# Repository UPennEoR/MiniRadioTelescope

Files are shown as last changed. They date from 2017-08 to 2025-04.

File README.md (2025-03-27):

# Mini Radio Telescope
MRT
A computerized telescope created using a satellite TV dish and hobbyist electronic components.<br/>
This GitHub contains Arduino and Python code for the telescope.

## Hardware
### Electronics
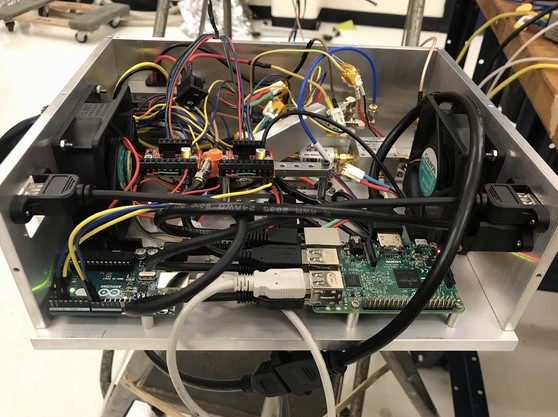
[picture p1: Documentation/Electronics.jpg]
Electronics

* Satellite Dish (with LNB)
* Arduino Uno
* Raspberry Pi
* [Stepper Motors](https://www.sparkfun.com/products/13656)
* [Big Easy Driver](https://www.sparkfun.com/products/12859)

### RF
* [Bias Tee](https://www.minicircuits.com/WebStore/dashboard.html?model=ZFBT-282-1.5A%2B)
* [Lumped LC High Pass Filter, 910 - 3000 MHz](https://www.minicircuits.com/WebStore/dashboard.html?model=SHP-900%2B)
* [LTCC Low Pass Filter, DC - 1200 MHz, 50Ω](https://www.minicircuits.com/WebStore/dashboard.html?model=VLF-1200%2B)
* [Power Detector](https://www.minicircuits.com/WebStore/dashboard.html?model=ZX47-60LN-S%2B)
* [Low Noise Amplifier, 40 - 2600 MHz, 50Ω](https://www.minicircuits.com/WebStore/dashboard.html?model=ZX60-P105LN%2B)
* [RTL-SDR](https://www.amazon.com/RTL-SDR-Blog-RTL2832U-Software-Defined/dp/B0129EBDS2/)

[Detailed Parts List](https://docs.google.com/spreadsheets/d/1V9u7jmuFzU5uZdgKm3iKv23dL2x4DQUVWW0j8lXsqZ8/edit?usp=sharing)

## Maps

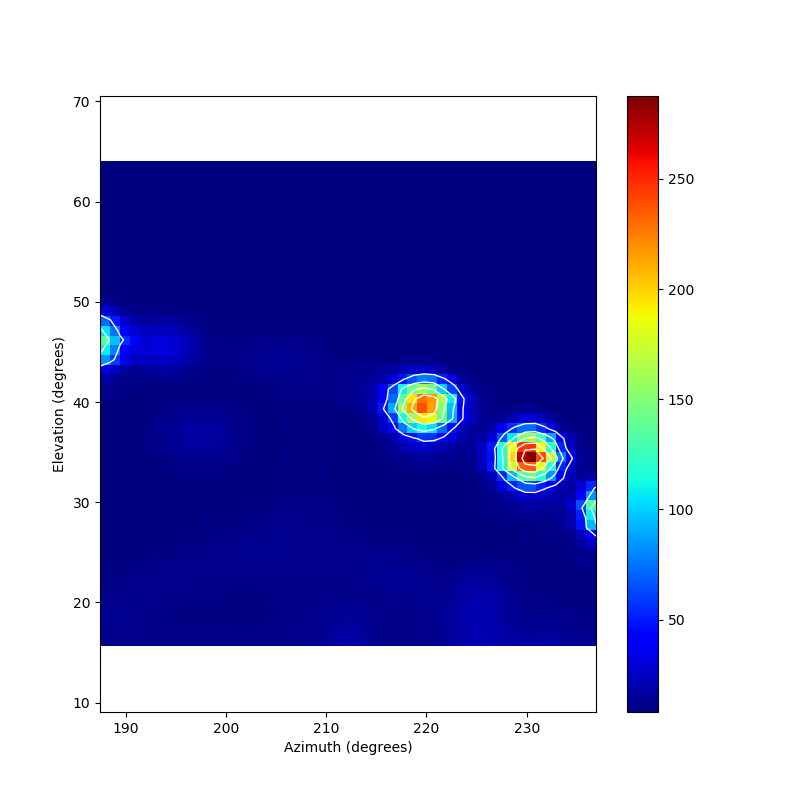
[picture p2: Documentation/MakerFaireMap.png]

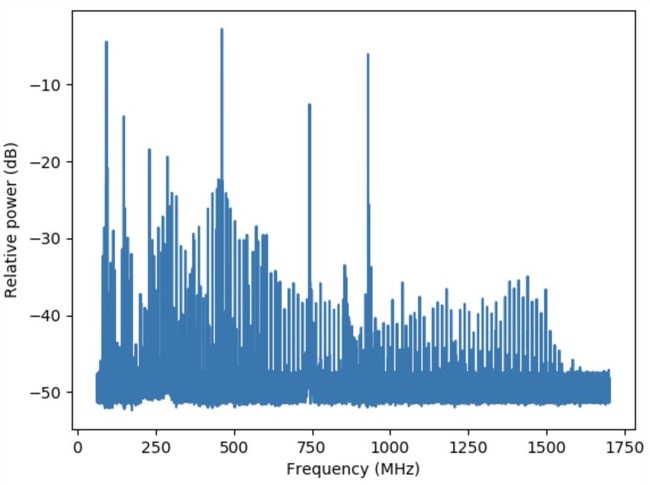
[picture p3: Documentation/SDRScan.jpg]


As of 5 April 2020, the working Arduino sketch is: MRTArduino (previously known as MRTv2)<br/>
The python code for the Pi is MRT_PY4.py

Hackaday was kind enough to do a write-up about this project: https://hackaday.com/2019/10/22/a-miniature-radio-telescope-in-every-backyard/

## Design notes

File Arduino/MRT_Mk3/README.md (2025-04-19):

This is the working version of the Arduino code as of 4/19/2025.  

There are a couple of numbers that are hardcoed:
- serial communication is at 115200 baud `BAUD_RATE`
- loop rate is 4 ms (250 Hz) `dt_loop`

The basic idea is that the Arduino loop continuously sends a certain set of information, namely
- the current counter value
- the number of milliseconds to complete the loop
- ~the last command sent~
- the current azimuth in motor microsteps (convertible but not converted to angle)
- the current elevation in motor microsteps (convertible but not converted to angle)
- the analog voltage at the AIN0 input
- a toggle bit for whether a (move) command is currently executing

Commands are 12 characters long and must be enclosed in <> as `<xxxxxxxxxxxx>`

<X> is the abort command, which stops all motion, and violates the 12 character rule.

Axis / Sense / Microstep / Clock cycles per step / Number of steps

0: 'a' azimuth or 'e' elevation
1: +/-
2: m: 1/16, e: 1/8 q: 1/4 h: 1/2 f: 1
3 - 6: the number of clock cycles 
7 - 11: number of steps.  This sets the max at one go to 99999

The C code necessary to read the Arduino output:

Install hdf5:
sudo apt install libhdf5-dev
sudo apt install hdf5-tools

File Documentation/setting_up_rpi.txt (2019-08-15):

Seems like Anaconda / Miniconda is not the way to go for RPi.

https://www.raspberrypi.org/documentation/linux/software/python.md

How to build a kind of minimal stack

https://geoffboeing.com/2016/03/scientific-python-raspberry-pi/

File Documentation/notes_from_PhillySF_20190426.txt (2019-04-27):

Arduino used previously lights up same as a working one, but I can't
seem to connect to it.  :( Not clear if this has anything to do with
powering it from the 9V regulator or not.

Now using
/anaconda3/bin/python
Working in base ... I might end up regretting that.
Note that this is a new Anaconda install since last used.

Apparently `serial` is not a standard install with Anaconda?

(base) modv-ve503-1809:MiniRadioTelescope jaguirre$ python MRT_PY3.py 
Traceback (most recent call last):
  File "MRT_PY3.py", line 6, in <module>
    import MRT_FUNC_PY3 as mrtf
  File "/Users/jaguirre/Software/MiniRadioTelescope/MRT_FUNC_PY3.py", line 8, in <module>
    import serial
ModuleNotFoundError: No module named 'serial'

conda install pyserial

DEATH TO PEOPLE WHO NAME THEIR PACKAGES DIFFERENT NAMES THAN THE IMPORT NAME!!!

Nice!  Not having the position sensor not connected is OK!

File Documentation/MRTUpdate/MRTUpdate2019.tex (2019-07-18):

\documentclass[11pt,letterpaper]{spie}

% Commonly used packages
\usepackage{natbib}
\usepackage{epsfig}
\usepackage{graphicx}
\usepackage{pgf}  
\usepackage{caption}
\usepackage{multirow}
\usepackage[normalem]{ulem}
\usepackage{color}
\usepackage{pdfpages}
\usepackage[breaklinks,colorlinks=true, pdfstartview=FitV, linkcolor=blue, 
            citecolor=blue, urlcolor=blue]{hyperref}
\usepackage{rotating}
\usepackage{url}
\usepackage{amsmath}
\usepackage{amssymb}
\usepackage{bm}

% Bibliography
%\bibliographystyle{apj_w_etal}
%\citestyle{aa}
%\include{journals}
%\pagenumbering{arabic}
%\pagestyle{plain}

\thispagestyle{empty}
% ------------------- Title and Author -----------------------------
\title{The Mini Radio Telescope (MRT):\\
A Tool for Education and Outreach}
%\author{James Aguirre}

\begin{document}

\maketitle

The Mini Radio Telescope funded by this grant is designed to be a portable demonstration and teaching tool.  This year it was was demonstrated at Boys' Latin High School, used in Prof. Aguirre's ASTR250 course at Penn, used as part of the Experimental Physics Research Academy summer program for high school students at Penn, and used in public demonstrations at the Philadelphia Science Festival both in Clark Park and on Philadelphia Parkway.

\begin{figure}[h]
\centering
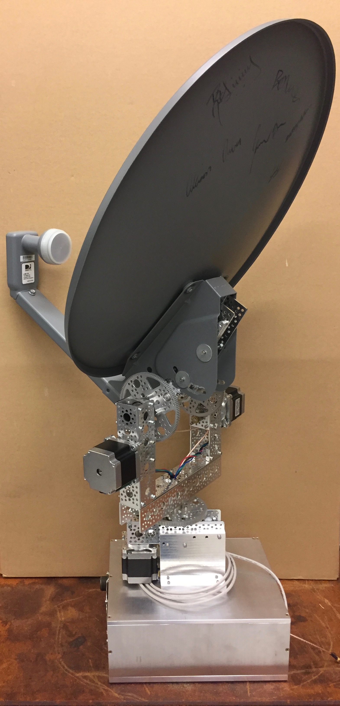
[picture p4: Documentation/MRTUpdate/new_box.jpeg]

\vspace{5pt}
\caption{The current mechanical design from hobby electronics components (Actobotics) was simple and quick, but insufficiently rigid.
}
\label{fig:Devices}
\end{figure}

\begin{figure}[h]
\centering
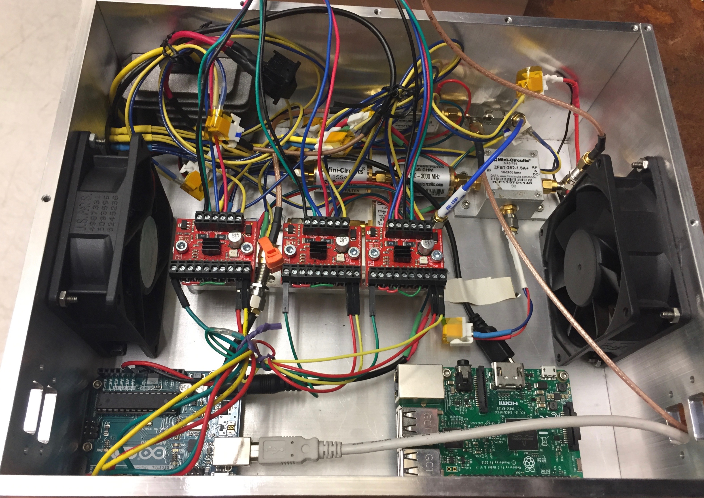
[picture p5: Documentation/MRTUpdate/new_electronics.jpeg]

\vspace{5pt}
\caption{The new electronics are housed in an enclosure designed to be more rugged.
}
\label{fig:Devices}
\end{figure}

\begin{figure}[h]
\centering
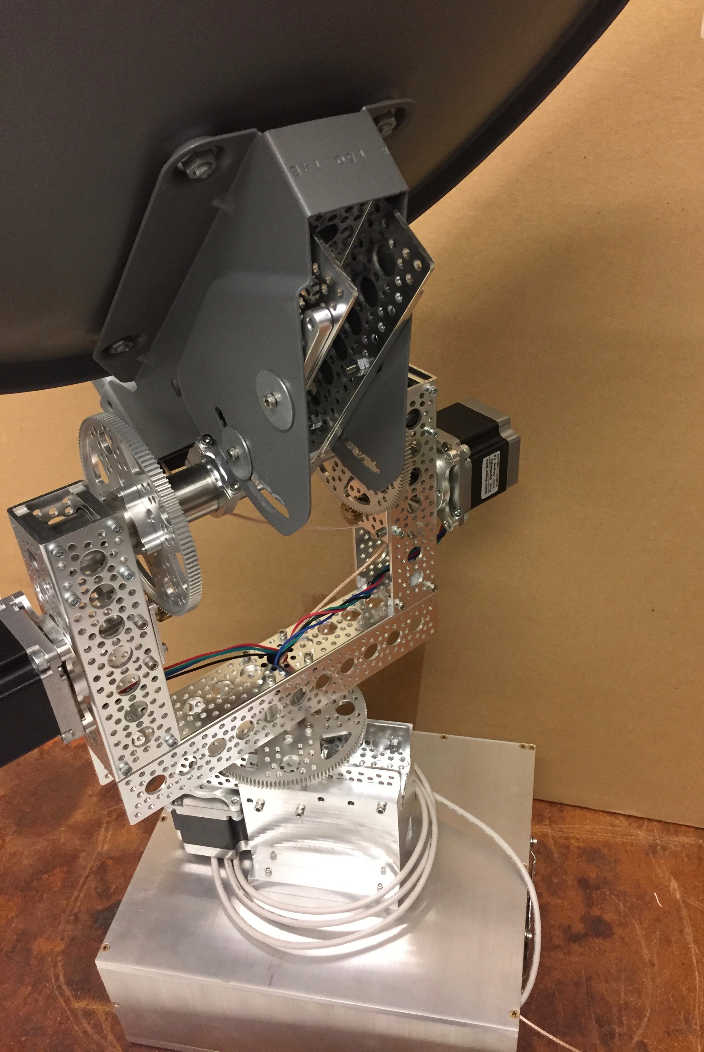
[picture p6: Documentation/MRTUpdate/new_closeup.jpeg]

\vspace{5pt}
\caption{The current mechanical design from hobby electronics components (Actobotics) was simple and quick, but insufficiently rigid.
}
\label{fig:Devices}
\end{figure}

\begin{figure}[h]
\centering
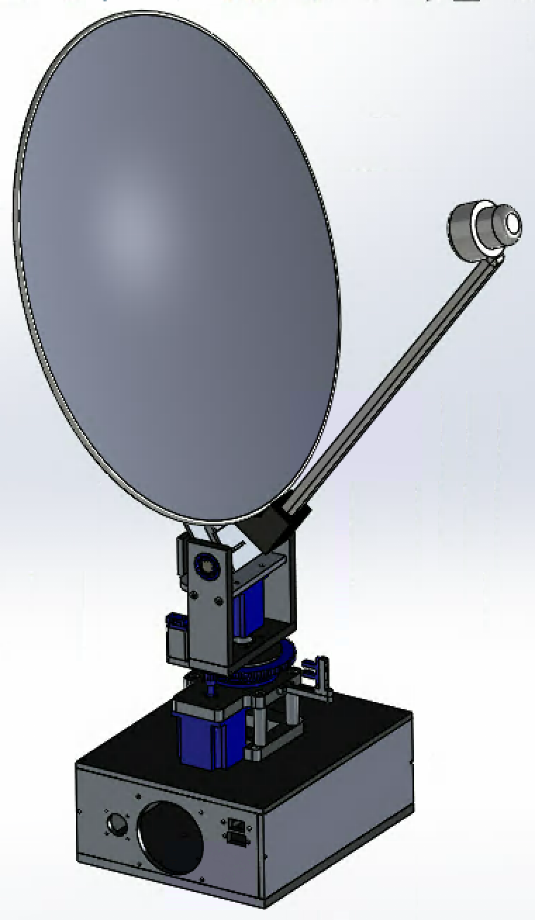
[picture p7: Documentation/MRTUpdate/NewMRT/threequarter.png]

\vspace{5pt}
\caption{The new simplified MRT telescope mount design.}
\label{fig:NewMRTthreequarter}
\end{figure}

\begin{figure}[h]
\centering
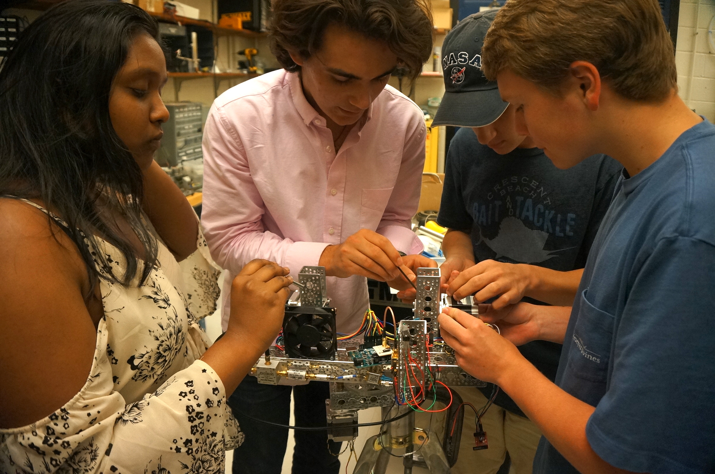
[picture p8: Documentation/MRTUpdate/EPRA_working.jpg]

\vspace{5pt}
\caption{EPRA students working on the MRT, summer 2017.}
\label{fig:Devices}
\end{figure}

\begin{figure}[h]
\centering
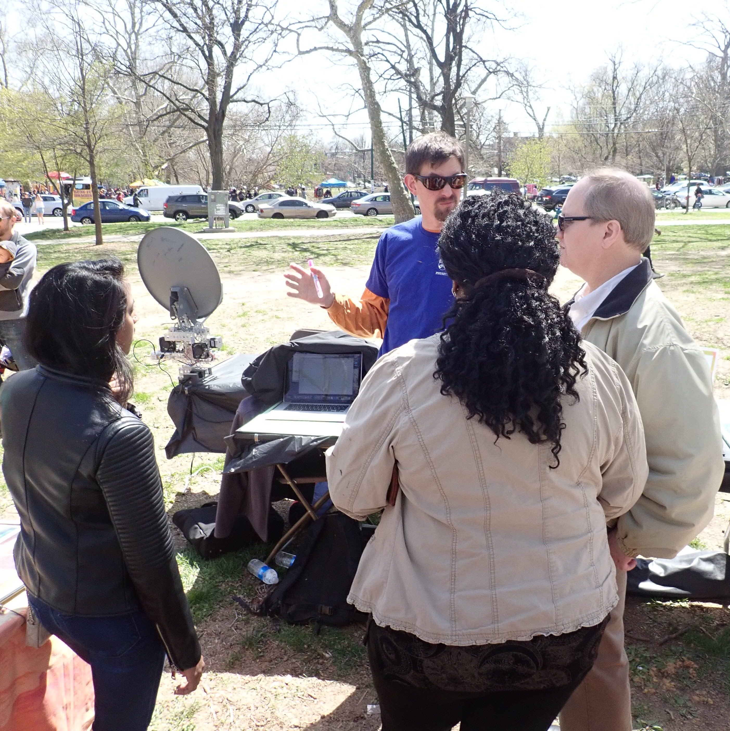
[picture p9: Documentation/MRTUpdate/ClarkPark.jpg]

\vspace{5pt}
\caption{Prof.~Aguirre with the MRT in Clark Park as part of the Philadelphia Science Festival, 21 April 2018.}
\label{fig:ClarkPark}
\end{figure}

\begin{figure}[h]
\centering
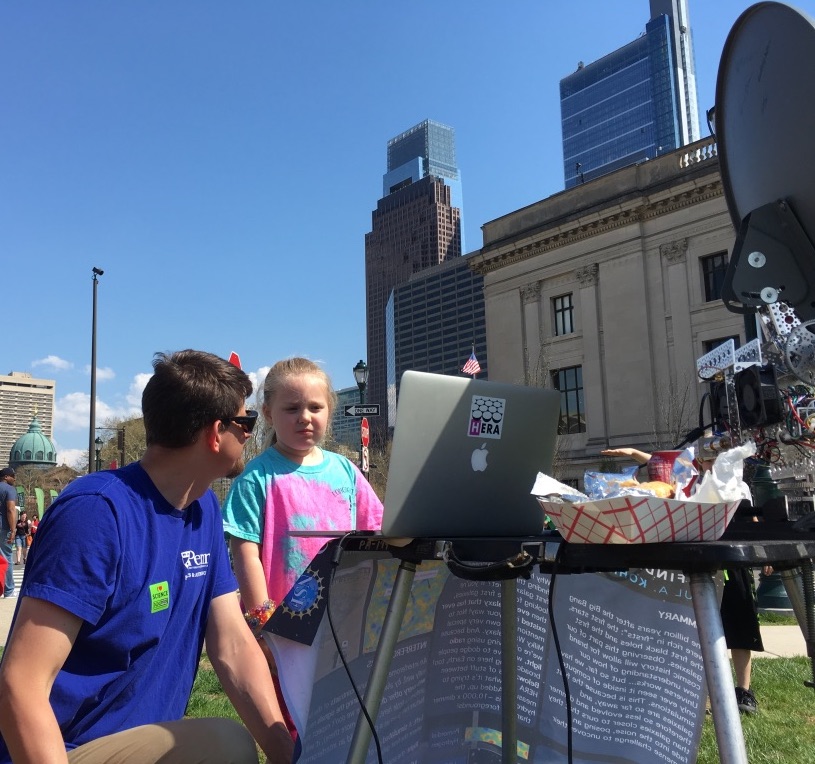
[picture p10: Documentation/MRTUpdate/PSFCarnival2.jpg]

\vspace{5pt}
\caption{Explaining the telescope to a young visitor to the Philadelphia Science Festival's Carnival, 28 April 2018.}
\label{fig:Devices}
\end{figure}

\end{document}

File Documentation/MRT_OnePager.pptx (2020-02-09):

## Mini Radio Telescope James Aguirre jaguirre@sas.upenn.edu Open source software at https://github.com/upenneor/miniradiotelescope

Raspberry Pi: runs the main control program and processes the data
Arduino: digitizes the signal from the radio receiver and communicates with the motor controllers to move the telescope
Radio filters and amplifiers: boost the signal from the commercial electronics and convert to a measurement of total power
Software defined radio (SDR): can make a spectrum of the received radio signal
Motor controllers: one for each axis of elevation and azimuth

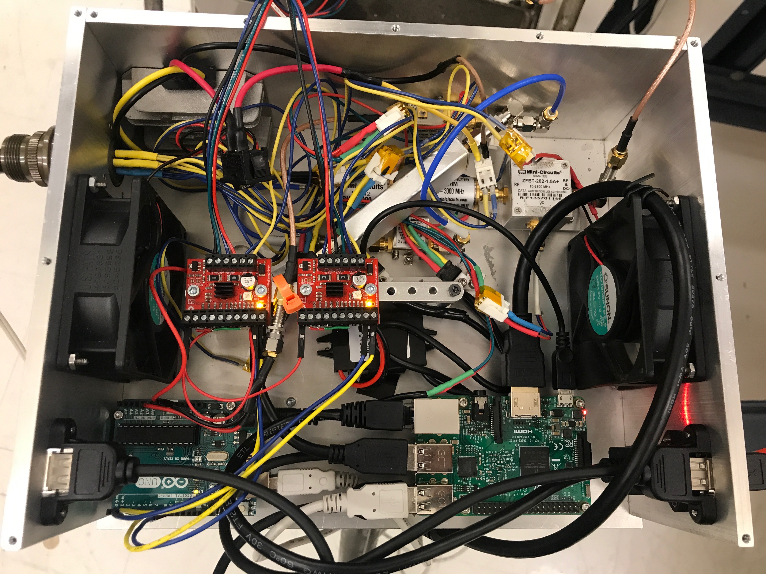
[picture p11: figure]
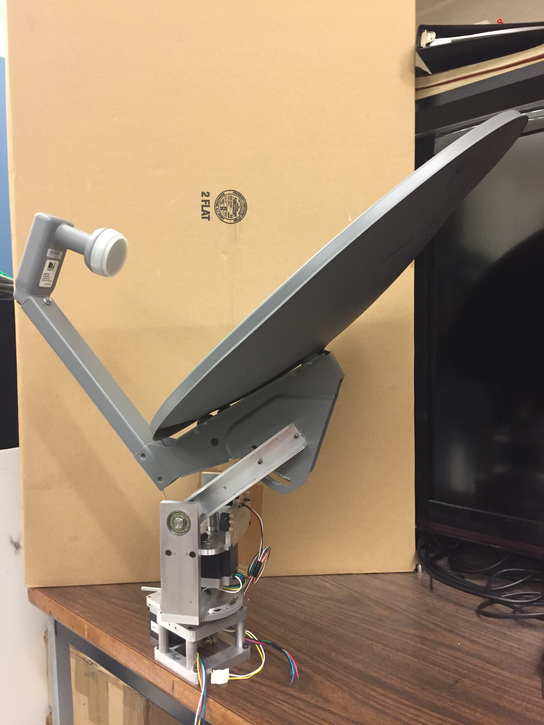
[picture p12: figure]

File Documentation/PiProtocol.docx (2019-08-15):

Raspberry Pi Set-up

On another (Linux) machine which can access the SD card:

Loading Operating System

1) To determine the name of the SD card

-Open Terminal

-type ‘df -h’ without the quotes before inserting card

-A list of mounted devices will appear

-Insert card and type ‘df -h’ again. The newly listed device is the name of the SD card.

-For example, ours was listed as ‘/dev/mmcblk0p1’

-Note: the name of the card is ‘mmcblk0’ and the partition designation is ‘p1’

2) Unmount card

-type ‘umount’ followed by the full name of your SD card

-For example, ours would be ‘ umount /dev/mmcblk0p1’

3) Download the latest OS released by Raspberry Pi

-At the time this is being written, the latest release is “Raspian Jessie with Pixel”

-This OS weighs 4.3 GB.

-Extract the file and make note of the name and location of the file

-Ex: ‘2016-09-23-raspian-jessie.img’ located under ‘/home/dmauri’

4) Install OS image on SD card

- ‘sudo dd bs=4M if=2016-09-23-raspian-jessie.img of=/dev/mmcblk0’

-sudo gives permission if you aren’t logged in as root

-USE CAUTION WHEN USING THE COMMAND dd

-If used improperly, the operating system on your current device can be erased

-After ‘if=’ type in the file name of the OS image to be loaded

-After ‘of=’ type in the name of the SD card without the partition index

-Note: At this point terminal will stop responding. It will not demonstrate how much progress has been made. To check on progress, open another Terminal window and type ‘sudo pkill -USR1 -n -x dd’

-When the system has finished writing the image to the card, it will generate a report such as:

‘1036+1 records in

1036+1 records out

4348444672 bytes (4.3 GB, 4.0 GiB) copied, 799.367 s, 5.4 MB/s

5) Synchronize and Eject Card

-type in ‘Sync’

-This will pull down everything that was left in the cache so that you can unmount

-Unmount card using the previously indicated umount command.

For the Pi itself:

Getting MAC Address

MAC Address is often required to establish Internet connection

1) In terminal type ‘ifconfig eth0’

-This will generate a report. Look for the the line:

‘eth0 Link encap: Ethernet HWaddr ’

-The characters following HWaddr is the MAC Address

Installing Arduino IDE

1) In terminal type ‘sudo apt-get install arduino’

-Installation will take time but upon completion can be accessed via terminal or from the menu.

Installing Miniconda

1) In terminal type the following in the listed order:

-‘wget http://repo.continuum.io/miniconda/Miniconda-3.5.5-Linux-armv6l.sh’

-‘md5sum Miniconda-3.5.5-Linux-armv6l.sh’

-This should return something like ‘2f37cb775ec3e482280a7bd6b97ee501’

-‘/bin/bash Miniconda-3.5.5-Linux-armv6l.sh’

Should also add git and emacs

sudo apt-get install git

Figuring out which port the Arduino is on

Hi Mauricio,

I’ve looked into making the ltr-sdr library that you pointed out yesterday. You can use the directions here: http://osmocom.org/projects/sdr/wiki/rtl-sdr. Basically the steps I followed were:

- git clone https://github.com/librtlsdr/librtlsdr.git

- cd librtlsdr

- mkdir build

- cd build

- cmake ../

- make

- sudo make install

- sudo ldconfig

This approach requires having `cmake` installed, so you might need to get that from somewhere. I also had to install `libusb`, which I did via MacPorts. Let me know if you have any questions about things, and we can work through them.

-Paul

Starting from scratch

Download NOOBS

https://www.raspberrypi.org/downloads/noobs/

(What is Raspberry Pi Desktop? https://www.raspberrypi.org/downloads/raspberry-pi-desktop/)

Needed a proper SD formatter

https://www.sdcard.org/downloads/formatter/

Formatted SD FAT-32

Copied NOOBS from unzipped file to SD

Booted RPi and chose Raspbian (only option if not connected online?)

(Scratch programming language?)

https://geoffboeing.com/2016/03/scientific-python-raspberry-pi/

For RTLSDR …

sudo apt-get install cmake

git clone https://github.com/librtlsdr/librtlsdr.git

cd librtlsdr

mkdir build

cd build

sudo apt-get install libusb-1.0

cmake ../ -DINSTALL_UDEV_RULES=ON -DDETACH_KERNEL_DRIVER=ON

make

sudo make install

sudo ldconfig

Installing jupyter

https://www.instructables.com/id/Jupyter-Notebook-on-Raspberry-Pi/

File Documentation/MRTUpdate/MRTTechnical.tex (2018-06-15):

\documentclass[11pt,letterpaper]{spie}

% Commonly used packages
\usepackage{natbib}
\usepackage{epsfig}
\usepackage{graphicx}
\usepackage{pgf}  
\usepackage{caption}
\usepackage{multirow}
\usepackage[normalem]{ulem}
\usepackage{color}
\usepackage{pdfpages}
\usepackage[breaklinks,colorlinks=true, pdfstartview=FitV, linkcolor=blue, 
            citecolor=blue, urlcolor=blue]{hyperref}
\usepackage{rotating}
\usepackage{url}
\usepackage{amsmath}
\usepackage{amssymb}
\usepackage{bm}

% Bibliography
%\bibliographystyle{apj_w_etal}
%\citestyle{aa}
%\include{journals}
%\pagenumbering{arabic}
%\pagestyle{plain}

\thispagestyle{empty}
% ------------------- Title and Author -----------------------------
\title{The Mini Radio Telescope (MRT):\\
Technical Update}
%\author{James Aguirre}

\begin{document}

\maketitle

The Mini Radio Telescope has now reached reasonable technical maturity, and we are working to make it completely robust for demonstrations, and capable of production in modest numbers.

The software is available publicly at \url{https://github.com/UPennEoR/MiniRadioTelescope}.

\begin{figure}[h]
\centering
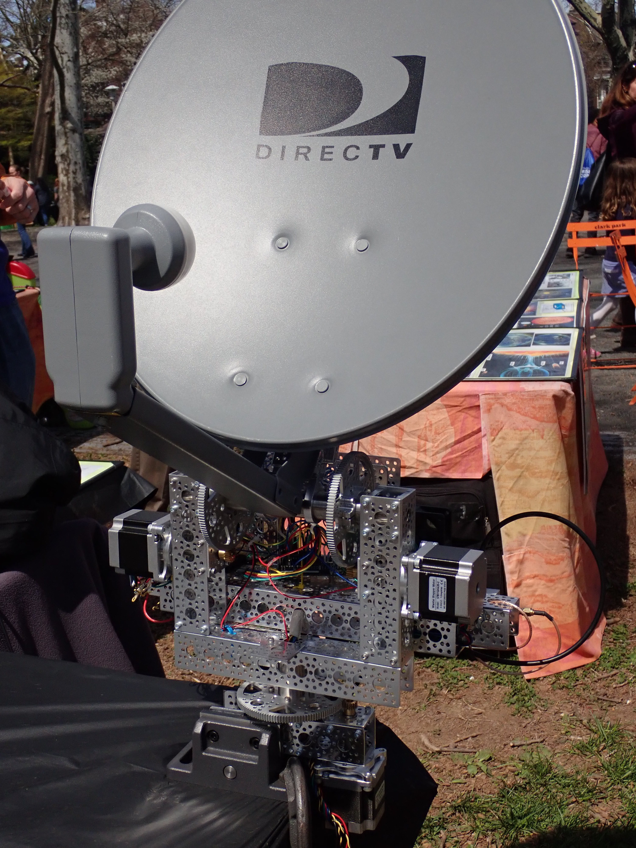
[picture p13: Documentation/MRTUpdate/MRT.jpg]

\vspace{5pt}
\caption{The Mini Radio Telescope in the spring of 2018.  All the components are commercially available and can be assembled with a minimal set of tools.}
\label{fig:Devices}
\end{figure}

\begin{figure}[h]
\centering
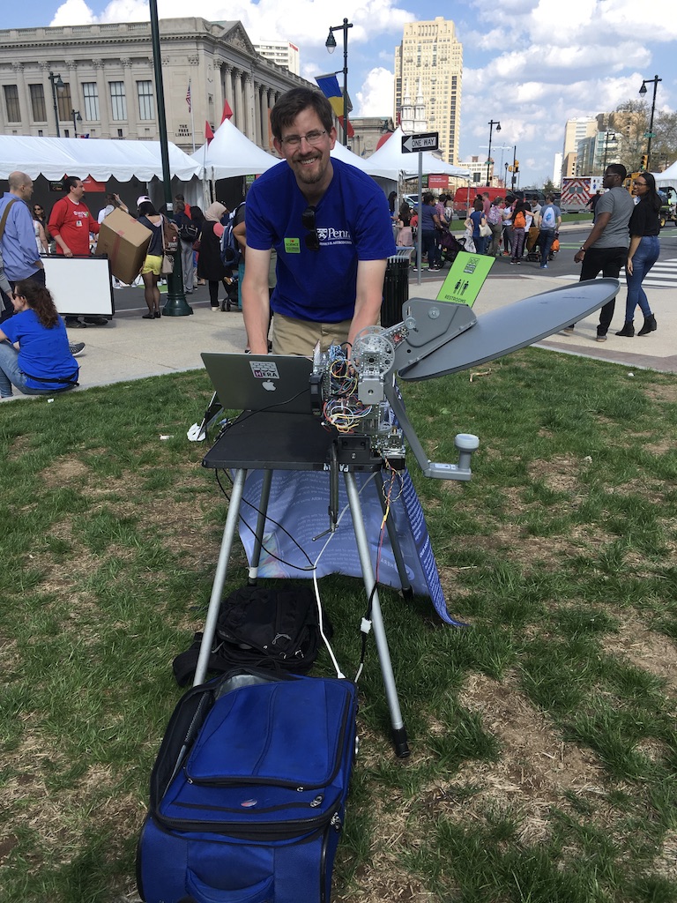
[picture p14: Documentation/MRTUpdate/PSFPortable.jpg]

\vspace{5pt}
\caption{The portable setup for the MRT on the Philadelphia Parkway for the Science Carnival.}
\label{fig:Devices}
\end{figure}

\begin{figure}[h]
\centering
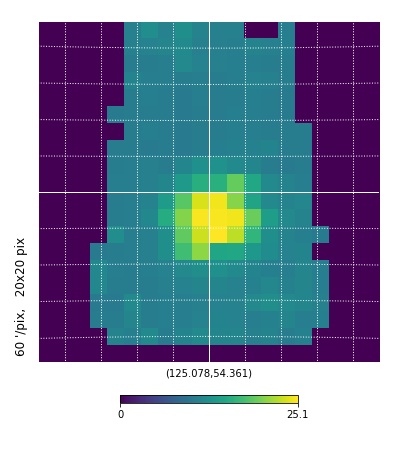
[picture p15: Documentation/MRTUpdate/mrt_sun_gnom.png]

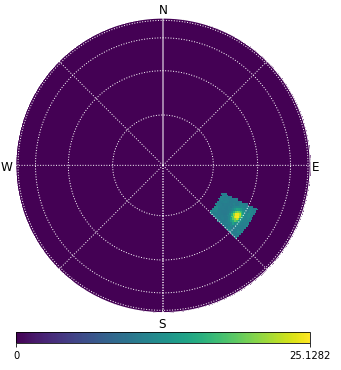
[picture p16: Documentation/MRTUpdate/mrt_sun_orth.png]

\vspace{5pt}
\caption{An MRT map of the sun.  Left: zoom in at the sun's location in altitude / elevation coordinates.   The resolution of the telescope ($5^\circ$) is larger than the true angular size of the sun ($0.5^\circ$).  Right: a view of the entire visible hemisphere showing the location of the mapped region.}
\label{fig:Sun}
\end{figure}

\begin{figure}[h]
\centering
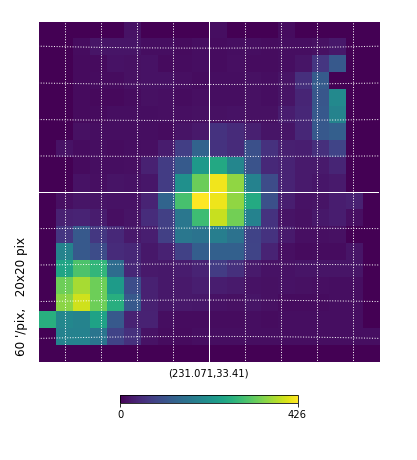
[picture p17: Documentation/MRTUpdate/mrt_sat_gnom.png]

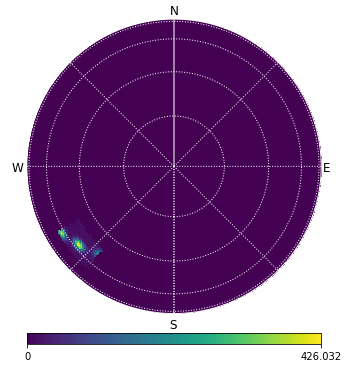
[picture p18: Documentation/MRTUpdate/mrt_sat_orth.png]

\vspace{5pt}
\caption{An MRT map of several geostationary satellites.  Same format as the Figure \ref{fig:Sun}.}
\label{fig:Satellites}
\end{figure}

%\bibliography{/Users/jaguirre/Documents/Latex/MasterReferences}

\end{document}

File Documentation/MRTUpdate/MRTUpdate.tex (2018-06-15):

\documentclass[11pt,letterpaper]{spie}

% Commonly used packages
\usepackage{natbib}
\usepackage{epsfig}
\usepackage{graphicx}
\usepackage{pgf}  
\usepackage{caption}
\usepackage{multirow}
\usepackage[normalem]{ulem}
\usepackage{color}
\usepackage{pdfpages}
\usepackage[breaklinks,colorlinks=true, pdfstartview=FitV, linkcolor=blue, 
            citecolor=blue, urlcolor=blue]{hyperref}
\usepackage{rotating}
\usepackage{url}
\usepackage{amsmath}
\usepackage{amssymb}
\usepackage{bm}

% Bibliography
%\bibliographystyle{apj_w_etal}
%\citestyle{aa}
%\include{journals}
%\pagenumbering{arabic}
%\pagestyle{plain}

\thispagestyle{empty}
% ------------------- Title and Author -----------------------------
\title{The Mini Radio Telescope (MRT):\\
A Tool for Education and Outreach}
%\author{James Aguirre}

\begin{document}

\maketitle

The Mini Radio Telescope funded by this grant is designed to be a portable demonstration and teaching tool.  This year it was was demonstrated at Boys' Latin High School, used in Prof. Aguirre's ASTR250 course at Penn, used as part of the Experimental Physics Research Academy summer program for high school students at Penn, and used in public demonstrations at the Philadelphia Science Festival both in Clark Park and on Philadelphia Parkway.

\begin{figure}[h]
\centering
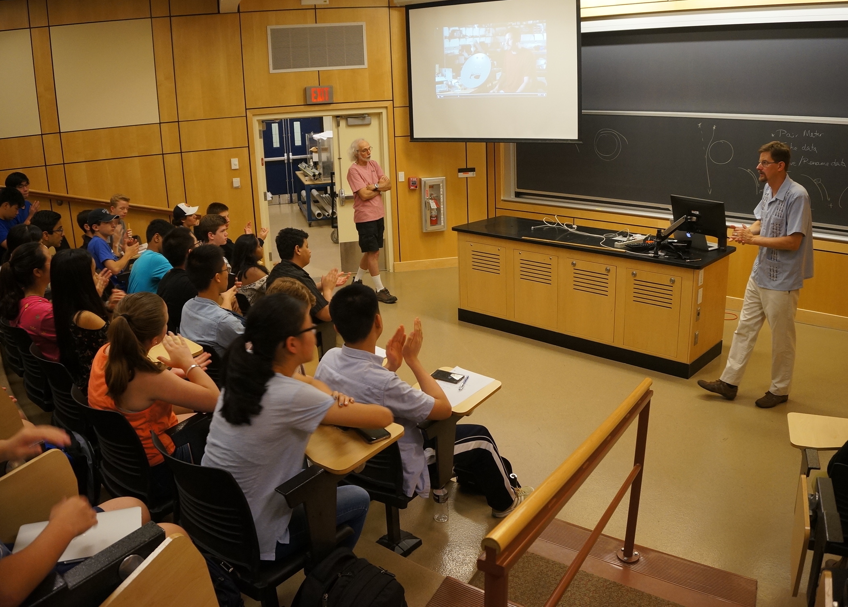
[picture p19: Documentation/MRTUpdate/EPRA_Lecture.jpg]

\vspace{5pt}
\caption{Prof.~Aguirre delivering a lecture to the high school students of the Experimental Physics Research Academy at Penn, Summer 2017.  
%The projected image is of the video describing his work at \url{https://penntoday.upenn.edu/spotlights/building-community-radio-telescope-west-philly}, but the video seems to have disappeared.
}
\label{fig:Devices}
\end{figure}

\begin{figure}[h]
\centering
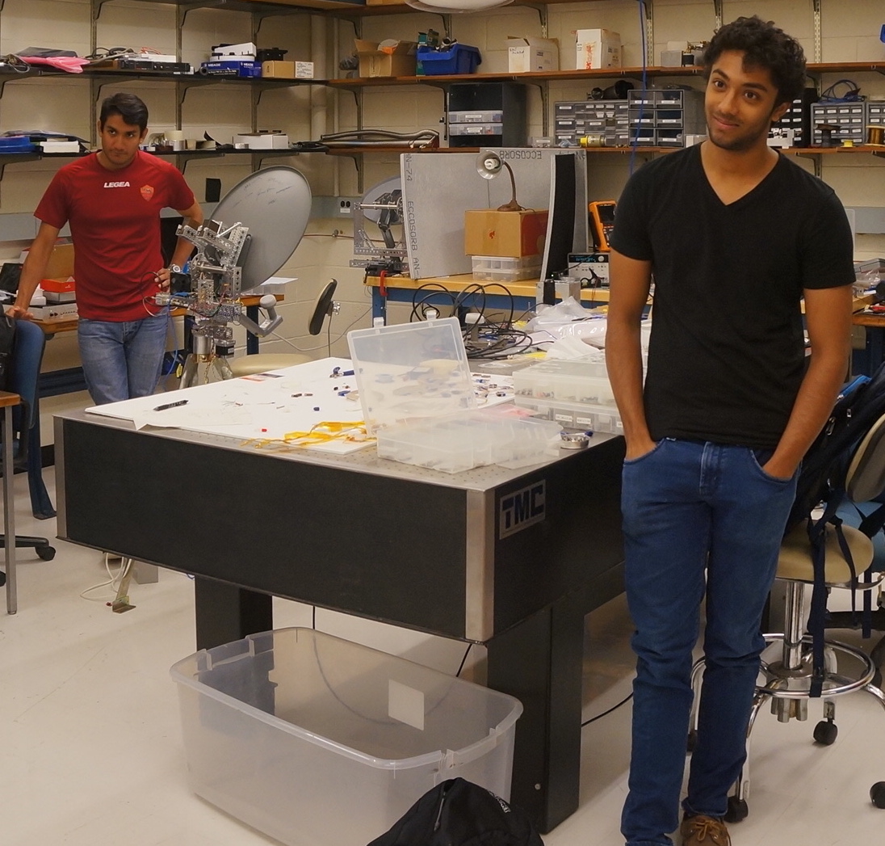
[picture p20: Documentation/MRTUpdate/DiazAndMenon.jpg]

\vspace{5pt}
\caption{Undergraduate research assistants Mauricio Diaz (left) and Viruj Menon (right) prepare to welcome the EPRA students.}
\label{fig:Devices}
\end{figure}

\begin{figure}[h]
\centering

\vspace{5pt}
\caption{EPRA students working on the MRT, summer 2017.}
\label{fig:Devices}
\end{figure}

\begin{figure}[h]
\centering

\vspace{5pt}
\caption{Prof.~Aguirre with the MRT in Clark Park as part of the Philadelphia Science Festival, 21 April 2018.}
\label{fig:ClarkPark}
\end{figure}

\begin{figure}[h]
\centering

\vspace{5pt}
\caption{Explaining the telescope to a young visitor to the Philadelphia Science Festival's Carnival, 28 April 2018.}
\label{fig:Devices}
\end{figure}

\end{document}

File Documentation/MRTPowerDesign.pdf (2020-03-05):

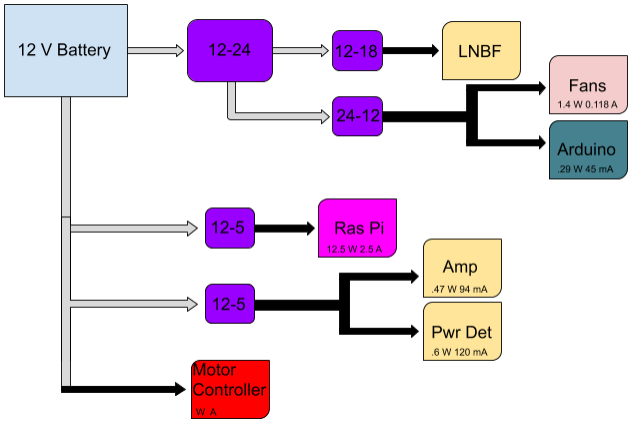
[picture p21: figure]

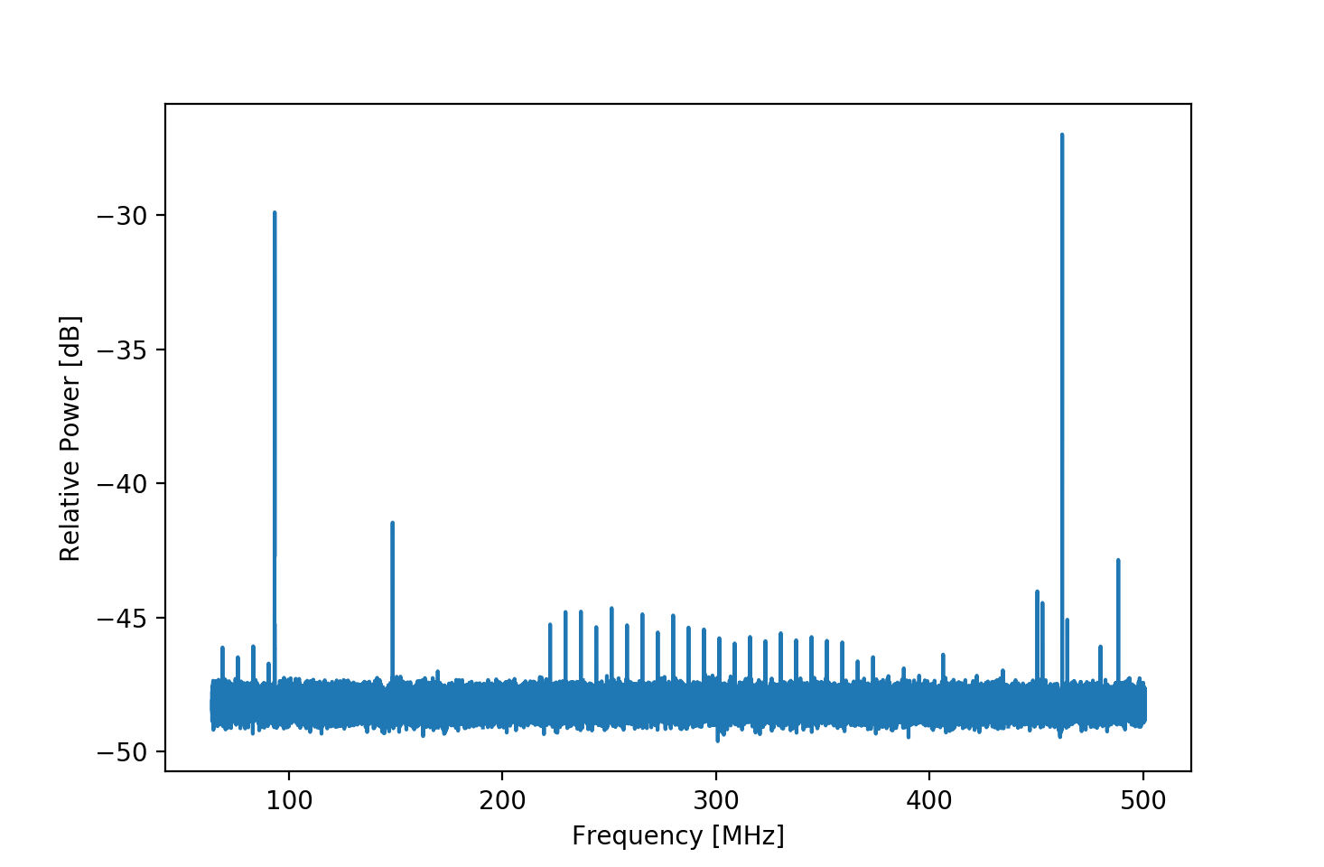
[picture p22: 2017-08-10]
Plots/SDR_Spectrum.png

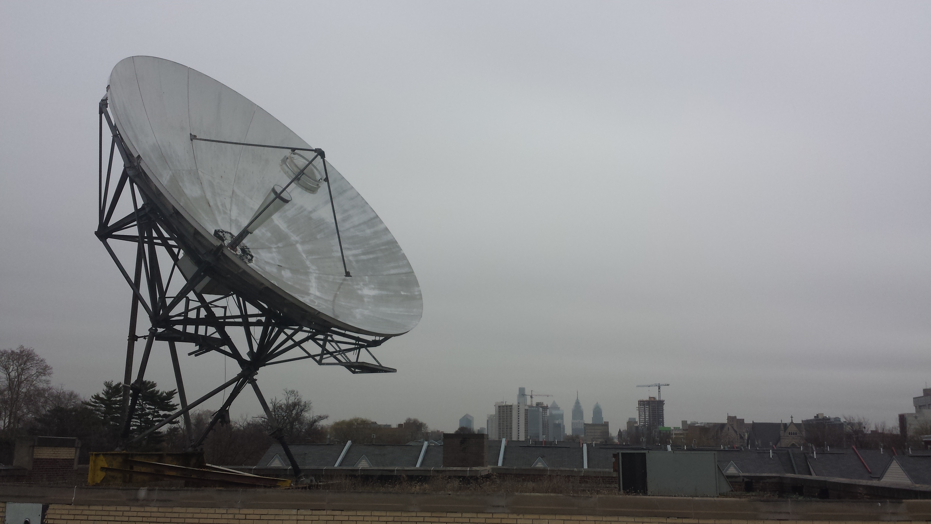
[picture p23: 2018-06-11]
PCRT/Design/Optics/TECDish/PCRT_Image_for_Scaffolding.jpg

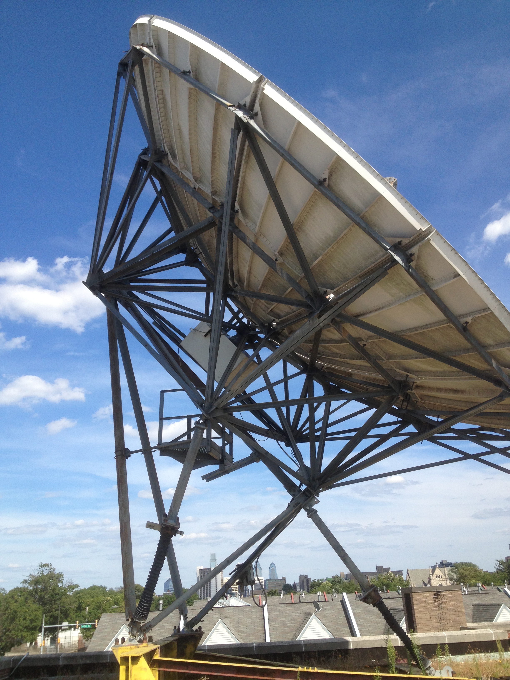
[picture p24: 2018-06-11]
PCRT/Design/Optics/TECDish/photo.JPG

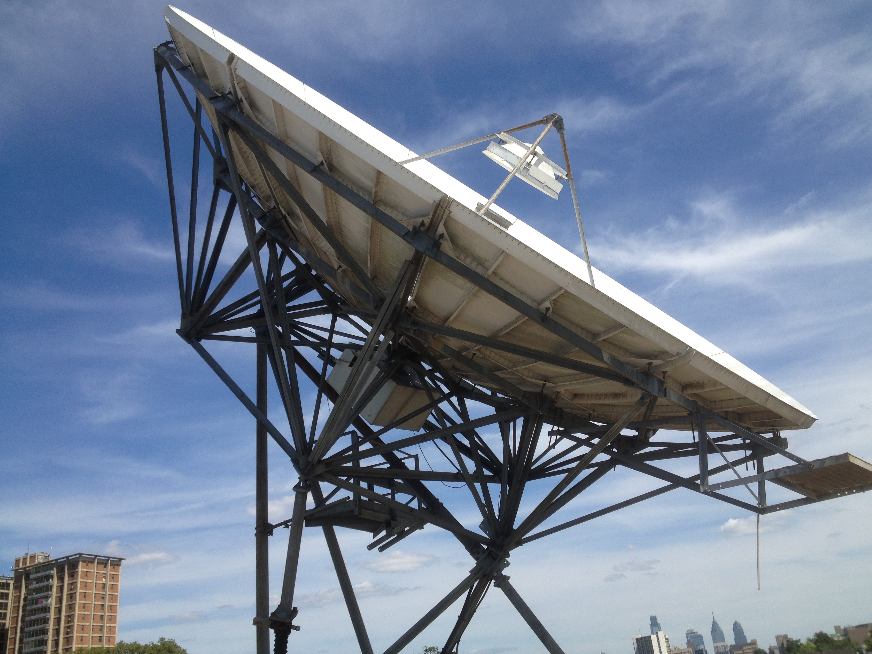
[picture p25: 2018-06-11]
PCRT/Design/Optics/TECDish/PCRT_Image_for_Optics_Determination.jpg

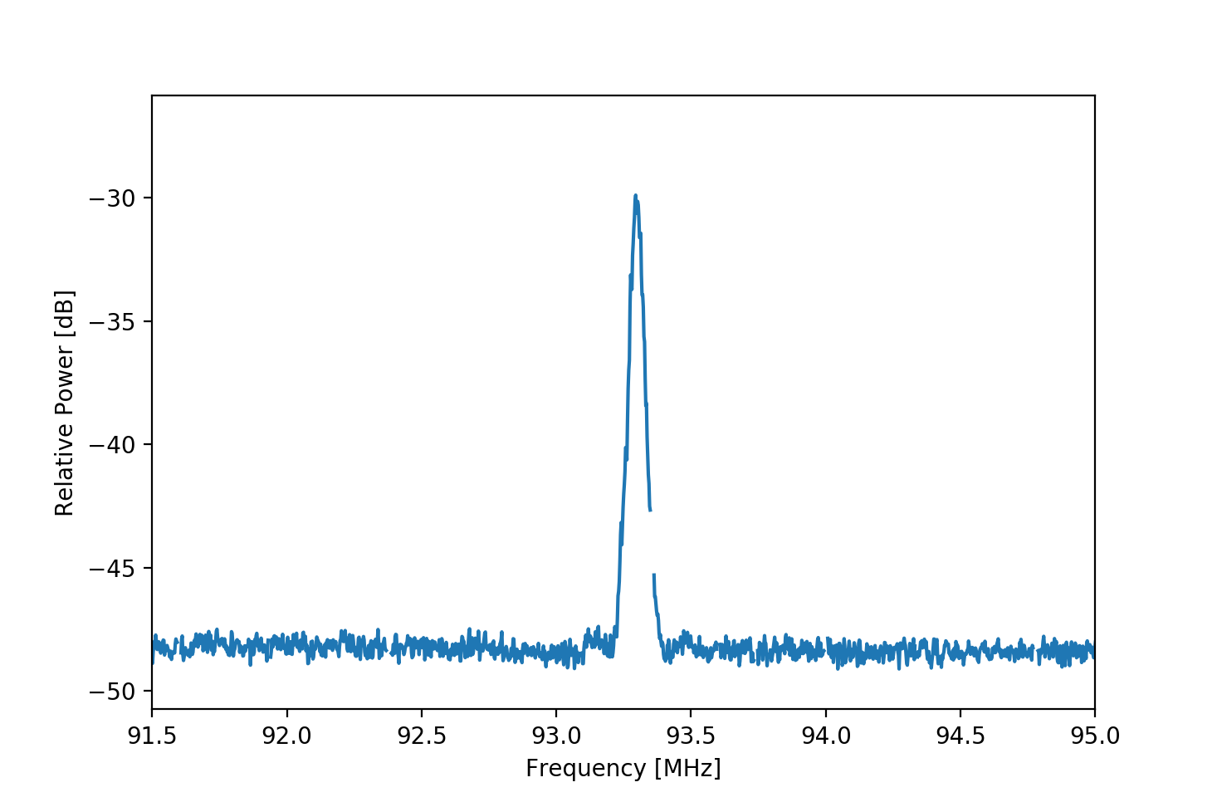
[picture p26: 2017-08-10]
Plots/SDR_Spectrum_Zoom1.png

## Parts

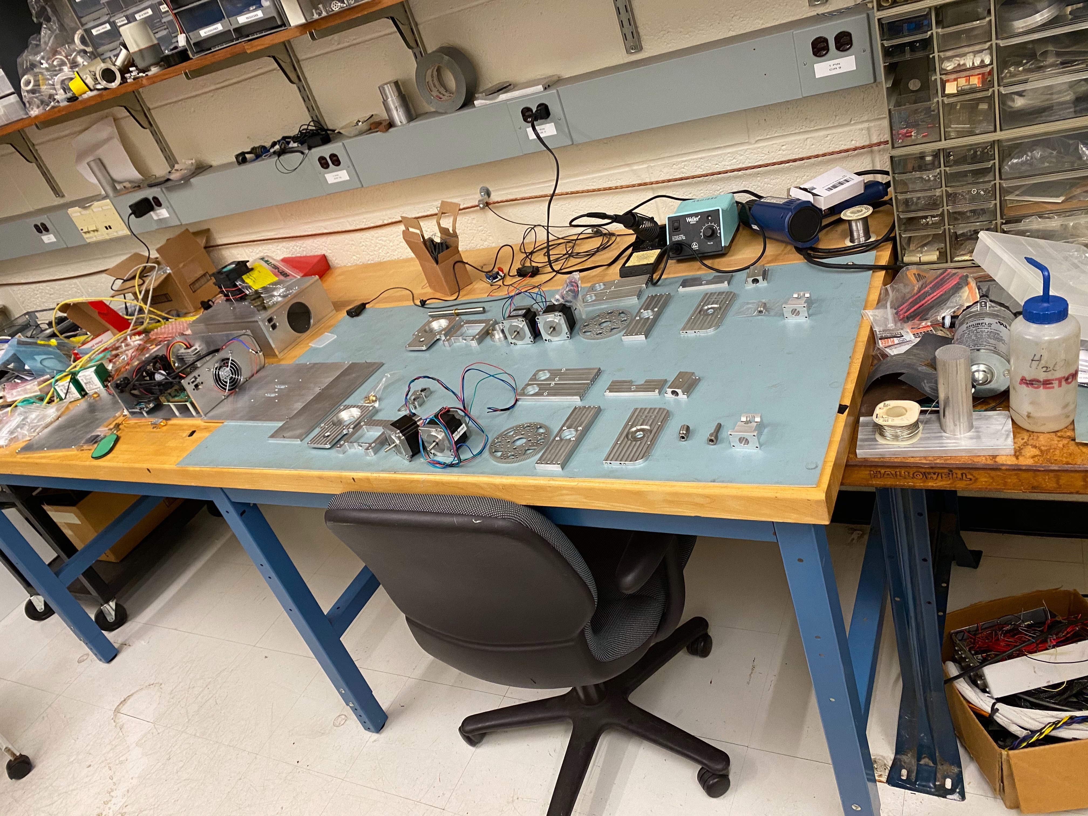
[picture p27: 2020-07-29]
Documentation/MRT_parts_July2020.jpg

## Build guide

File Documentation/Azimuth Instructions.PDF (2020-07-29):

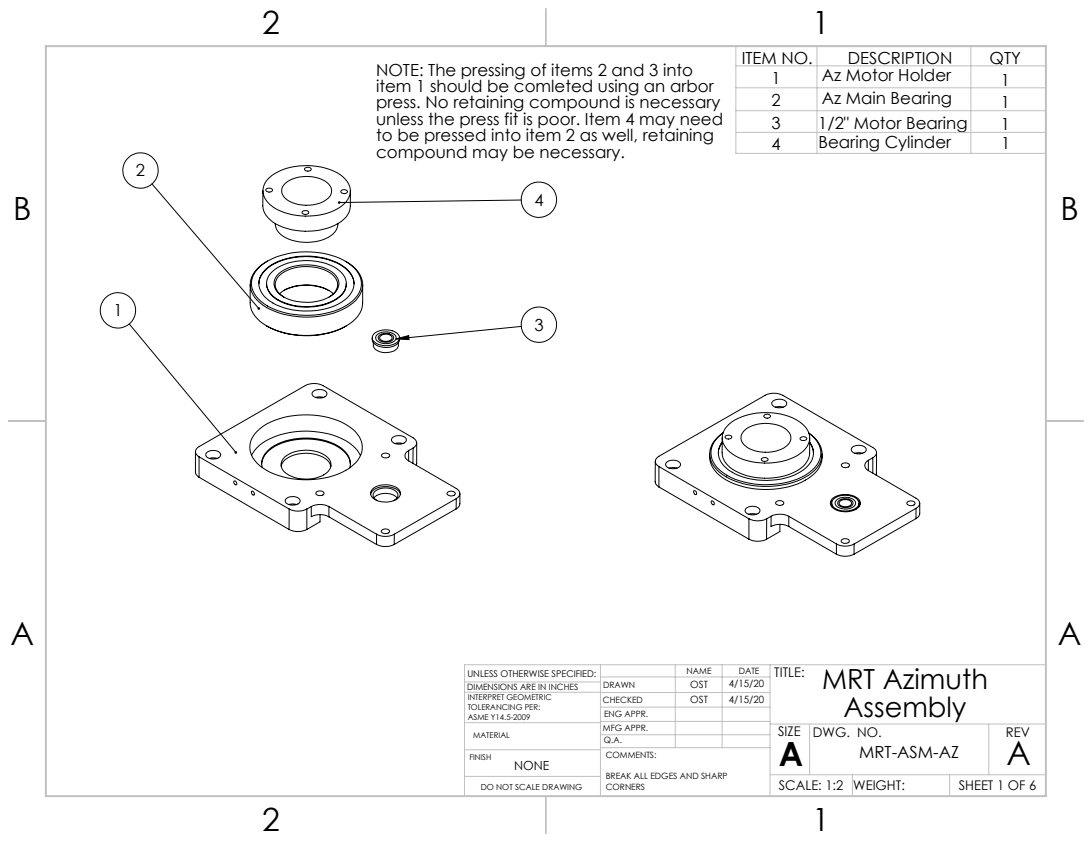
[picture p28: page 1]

ITEM NO. | DESCRIPTION | QTY
1 | Az Motor Holder | 1
2 | Az Main Bearing | 1
3 | 1/2" Motor Bearing | 1
4 | Bearing Cylinder | 1

NOTE: The pressing of items 2 and 3 into
item 1 should be comleted using an arbor
press. No retaining compound is necessary
unless the press fit is poor. Item 4 may need
to be pressed into item 2 as well, retaining
compound may be necessary.

UNLESS OTHERWISE SPECIFIED: | | NAME | DATE | MRT Azimuth TITLE: Assembly
MATERIAL | MFG APPR. | | | SIZE A | DWG. NO. MRT-ASM-AZ | REV A

DRAWN | OST | 4/15/20

DIMENSIONS ARE IN INCHES

INTERPRET GEOMETRIC TOLERANCING PER: ASME Y14.5-2009 | CHECKED | OST | 4/15/20

ENG APPR.

NONE FINISH | COMMENTS: BREAK ALL EDGES AND SHARP CORNERS

DO NOT SCALE DRAWING | | SCALE: 1:2 | WEIGHT: | SHEET 1 OF 6

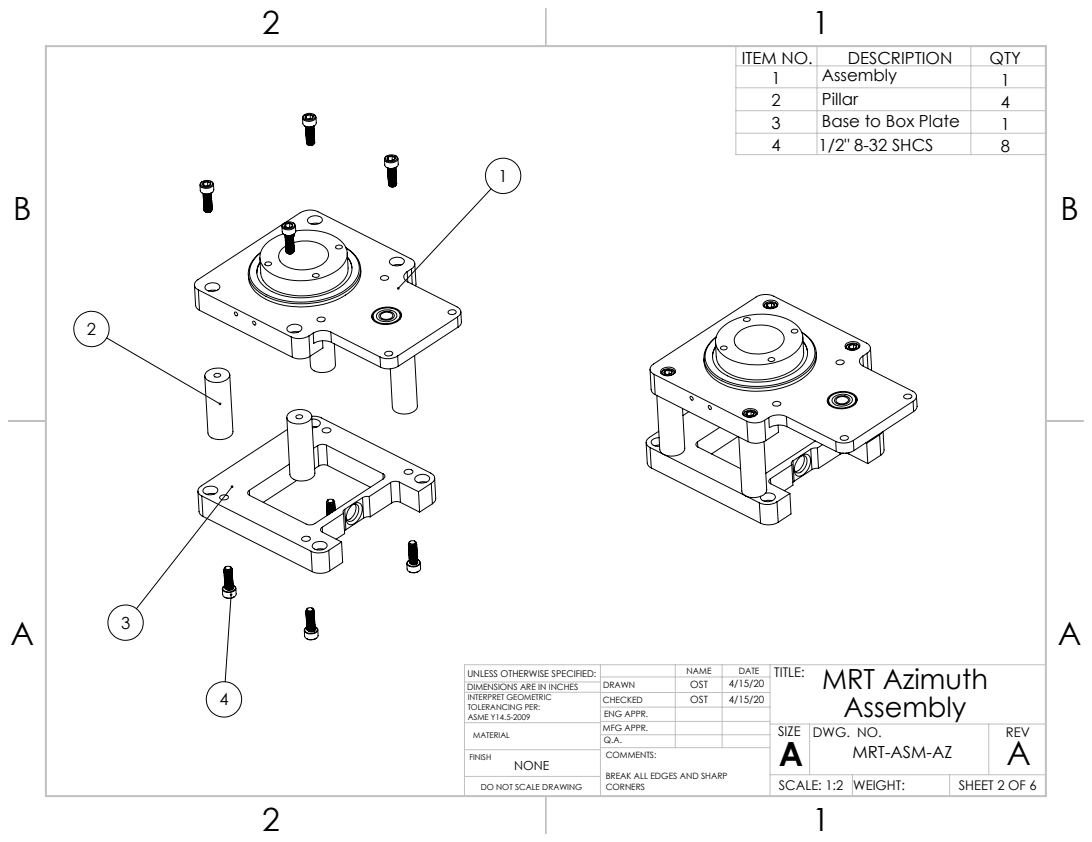
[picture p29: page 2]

1 | Assembly | 1
2 | Pillar | 4
3 | Base to Box Plate | 1
4 | 1/2" 8-32 SHCS | 8

UNLESS OTHERWISE SPECIFIED: | | NAME | DATE | MRT Azimuth TITLE: Assembly
MATERIAL | MFG APPR. | | | SIZE A | DWG. NO. MRT-ASM-AZ | REV A

DRAWN | OST | 4/15/20

DIMENSIONS ARE IN INCHES

INTERPRET GEOMETRIC TOLERANCING PER: ASME Y14.5-2009 | CHECKED | OST | 4/15/20

ENG APPR.

NONE FINISH | COMMENTS:

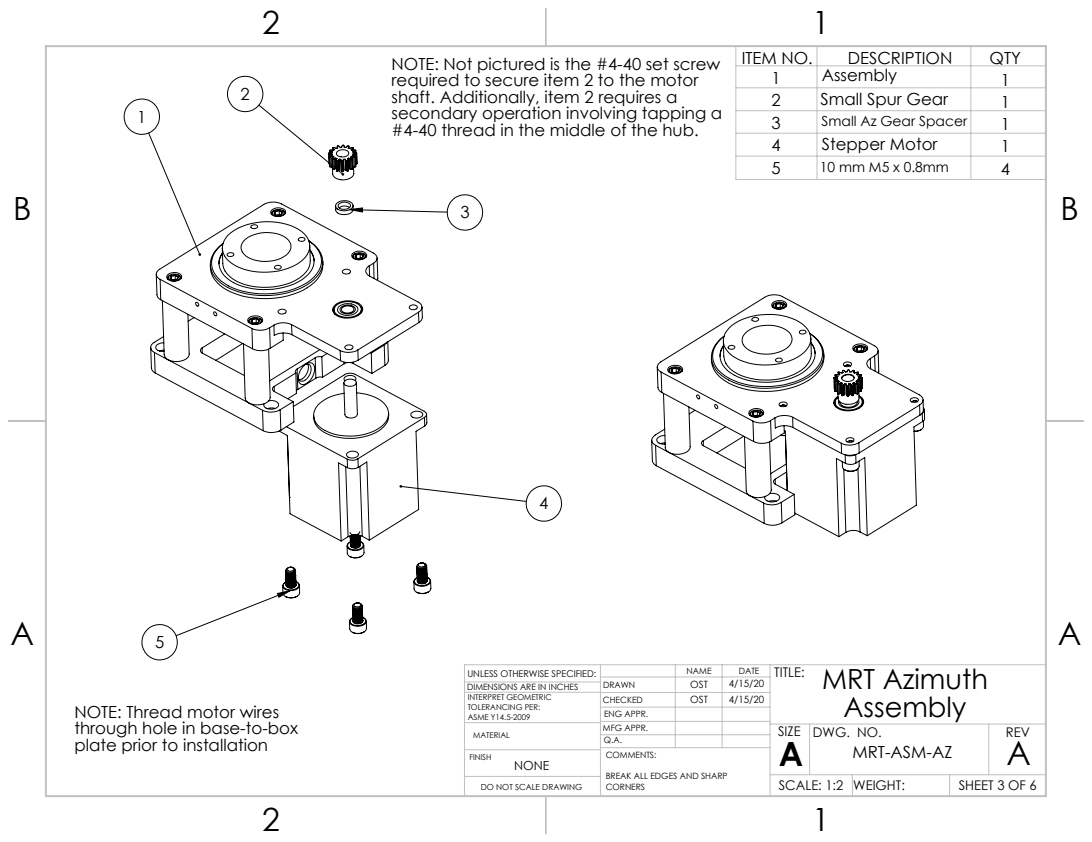
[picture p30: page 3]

NOTE: Not pictured is the #4-40 set screw
required to secure item 2 to the motor
shaft. Additionally, item 2 requires a
secondary operation involving tapping a
#4-40 thread in the middle of the hub.

1 | Assembly | 1
2 | Small Spur Gear | 1
3 | Small Az Gear Spacer | 1
4 | Stepper Motor | 1
5 | 10 mm M5 x 0.8mm | 4

UNLESS OTHERWISE SPECIFIED: | | NAME | DATE | MRT Azimuth TITLE: Assembly
MATERIAL | MFG APPR. | | | SIZE A | DWG. NO. MRT-ASM-AZ | REV A

DRAWN | OST | 4/15/20

DIMENSIONS ARE IN INCHES

NOTE: Thread motor wires
through hole in base-to-box
plate prior to installation

INTERPRET GEOMETRIC TOLERANCING PER: ASME Y14.5-2009 | CHECKED | OST | 4/15/20

ENG APPR.

NONE FINISH | COMMENTS:

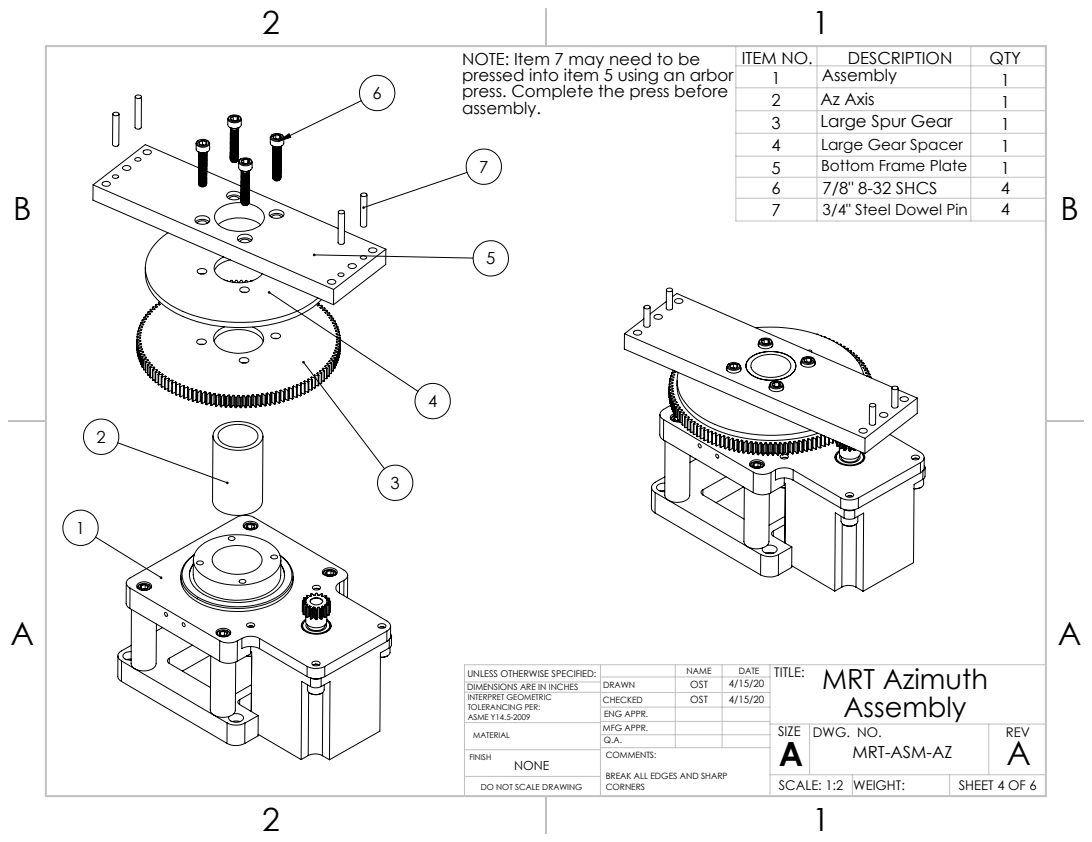
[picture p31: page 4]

NOTE: Item 7 may need to be
pressed into item 5 using an arbor
press. Complete the press before
assembly.

1 | Assembly | 1
2 | Az Axis | 1
3 | Large Spur Gear | 1
4 | Large Gear Spacer | 1
5 | Bottom Frame Plate | 1
6 | 7/8" 8-32 SHCS | 4
7 | 3/4" Steel Dowel Pin | 4

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

DRAWN | OST | 4/15/20

DIMENSIONS ARE IN INCHES

INTERPRET GEOMETRIC TOLERANCING PER: ASME Y14.5-2009 | CHECKED | OST | 4/15/20

ENG APPR.

NONE FINISH | COMMENTS:

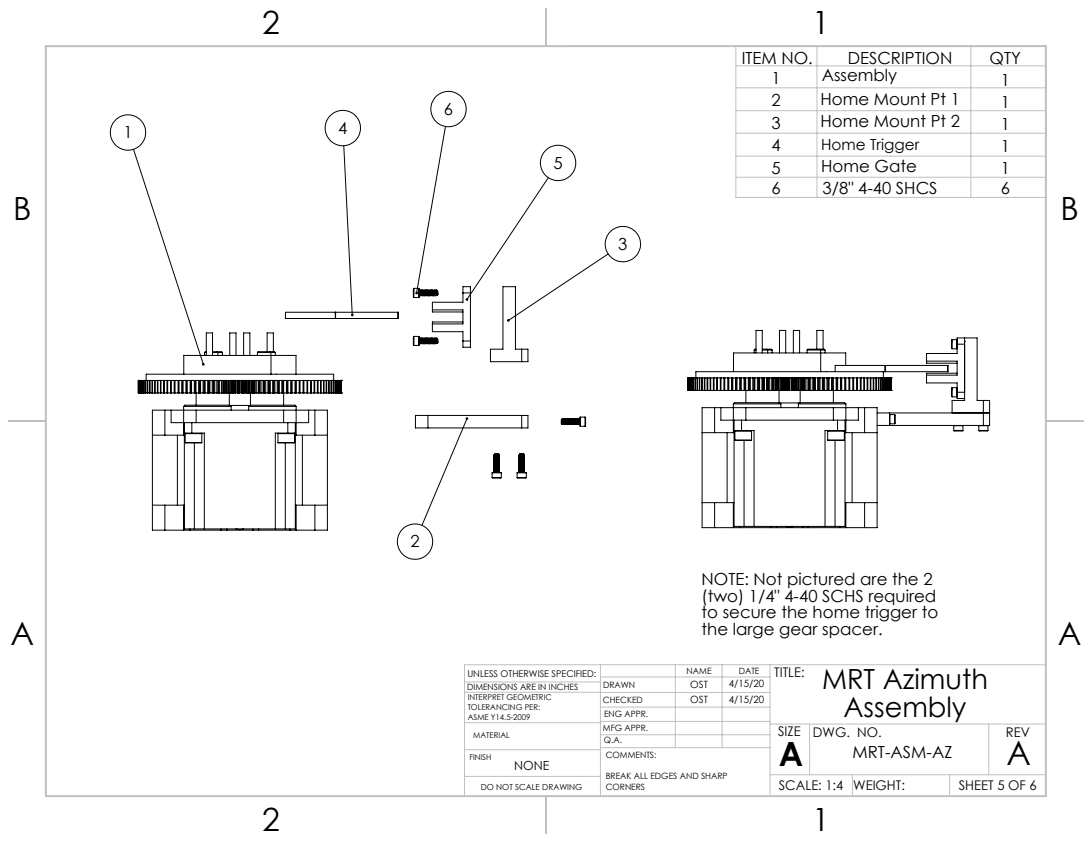
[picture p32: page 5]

1 | Assembly | 1
2 | Home Mount Pt 1 | 1
3 | Home Mount Pt 2 | 1
4 | Home Trigger | 1
5 | Home Gate | 1
6 | 3/8" 4-40 SHCS | 6

NOTE: Not pictured are the 2
(two) 1/4" 4-40 SCHS required
to secure the home trigger to
the large gear spacer.

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

DRAWN | OST | 4/15/20

DIMENSIONS ARE IN INCHES

INTERPRET GEOMETRIC TOLERANCING PER: ASME Y14.5-2009 | CHECKED | OST | 4/15/20

ENG APPR.

NONE FINISH | COMMENTS:

SCALE: 1:4 | WEIGHT:

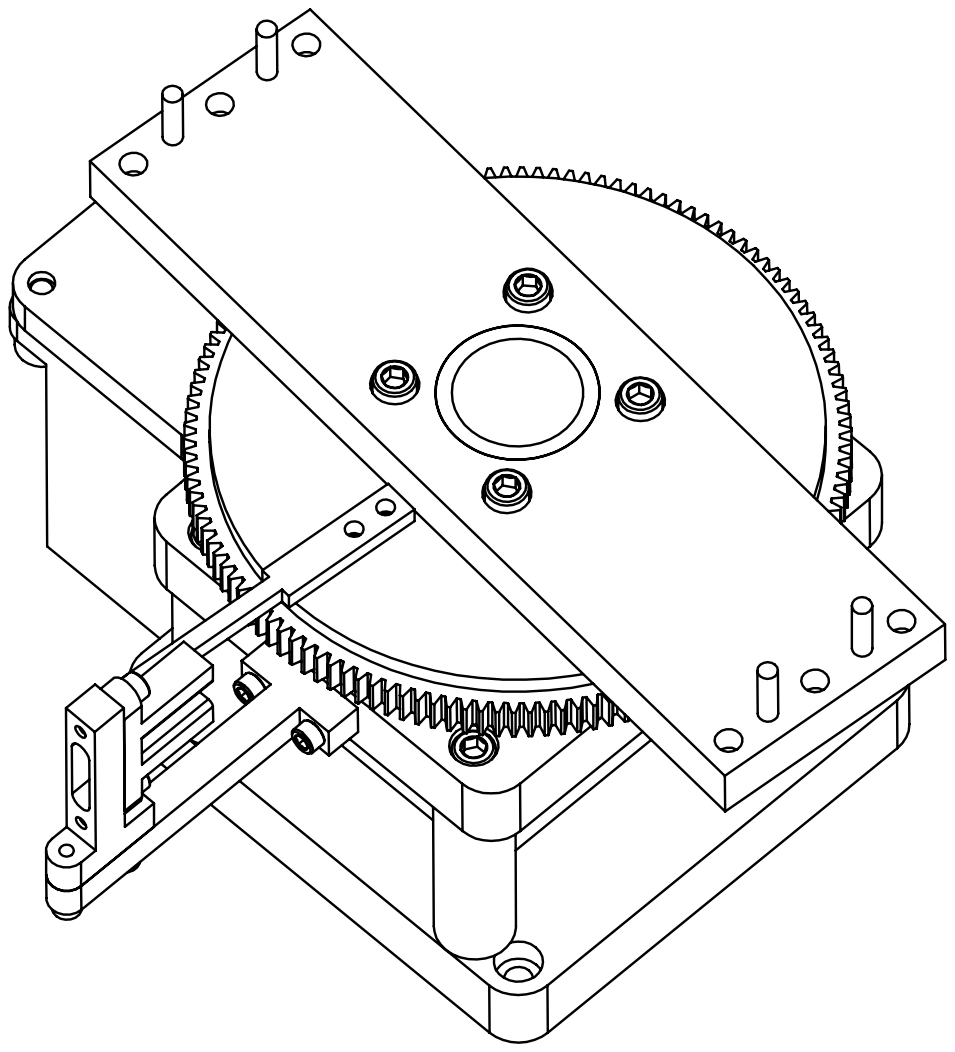
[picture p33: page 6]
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

DRAWN | OST | 4/15/20

DIMENSIONS ARE IN INCHES

INTERPRET GEOMETRIC TOLERANCING PER: ASME Y14.5-2009 | CHECKED | OST | 4/15/20

ENG APPR.

NONE FINISH | COMMENTS:

SCALE: 2:3 | WEIGHT:

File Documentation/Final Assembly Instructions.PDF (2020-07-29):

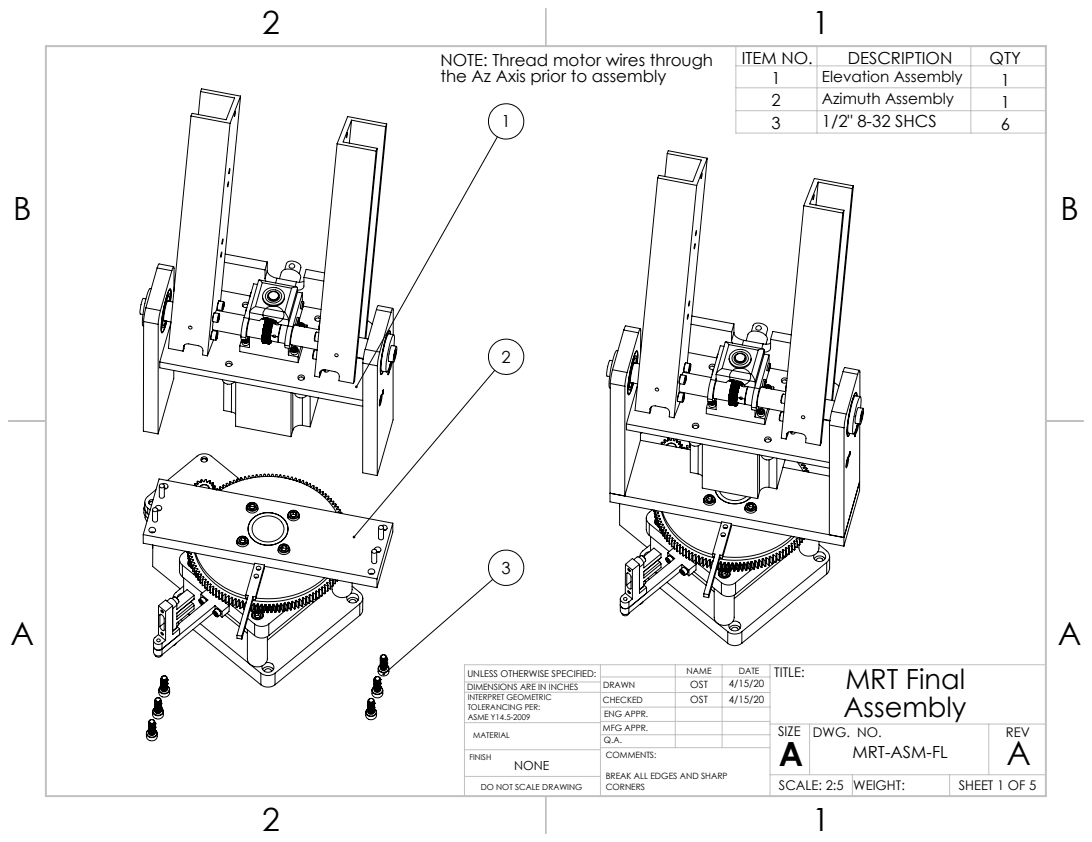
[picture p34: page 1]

NOTE: Thread motor wires through
the Az Axis prior to assembly

ITEM NO. | DESCRIPTION | QTY
1 | Elevation Assembly | 1
2 | Azimuth Assembly | 1
3 | 1/2" 8-32 SHCS | 6

UNLESS OTHERWISE SPECIFIED: | | NAME | DATE | MRT Final TITLE: Assembly
MATERIAL | MFG APPR. | | | SIZE A | DWG. NO. MRT-ASM-FL | REV A

DRAWN | OST | 4/15/20

DIMENSIONS ARE IN INCHES

INTERPRET GEOMETRIC TOLERANCING PER: ASME Y14.5-2009 | CHECKED | OST | 4/15/20

ENG APPR.

NONE FINISH | COMMENTS: BREAK ALL EDGES AND SHARP CORNERS

DO NOT SCALE DRAWING | | SCALE: 2:5 | WEIGHT: | SHEET 1 OF 5

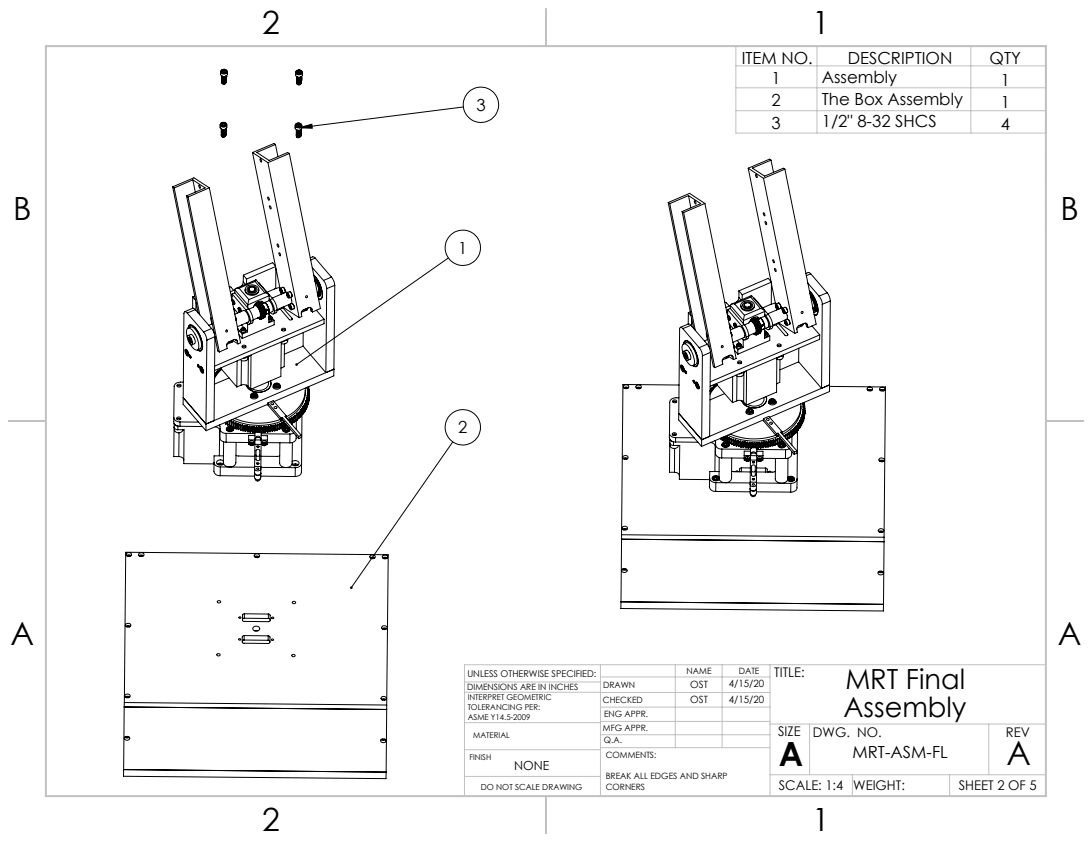
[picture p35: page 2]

1 | Assembly | 1
2 | The Box Assembly | 1
3 | 1/2" 8-32 SHCS | 4

UNLESS OTHERWISE SPECIFIED: | | NAME | DATE | MRT Final TITLE: Assembly
MATERIAL | MFG APPR. | | | SIZE A | DWG. NO. MRT-ASM-FL | REV A

DRAWN | OST | 4/15/20

DIMENSIONS ARE IN INCHES

INTERPRET GEOMETRIC TOLERANCING PER: ASME Y14.5-2009 | CHECKED | OST | 4/15/20

ENG APPR.

NONE FINISH | COMMENTS:

SCALE: 1:4 | WEIGHT:

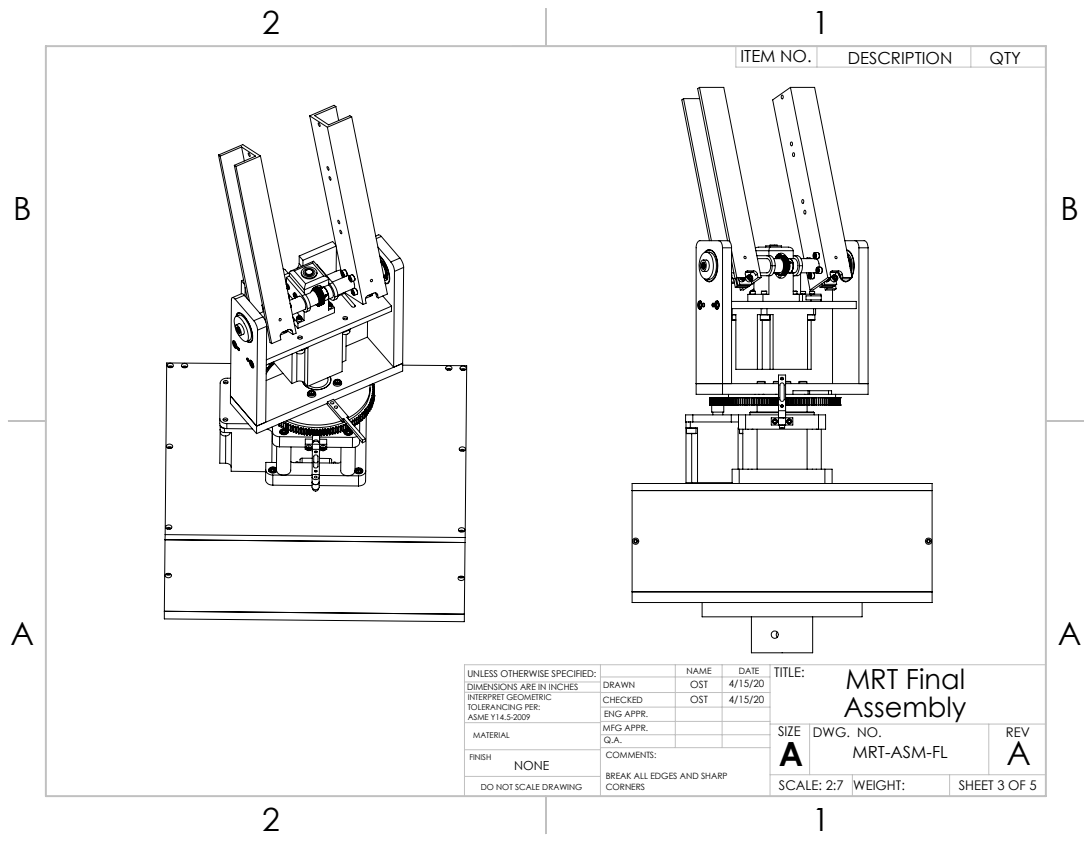
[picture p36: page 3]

UNLESS OTHERWISE SPECIFIED: | | NAME | DATE | MRT Final TITLE: Assembly
MATERIAL | MFG APPR. | | | SIZE A | DWG. NO. MRT-ASM-FL | REV A

DRAWN | OST | 4/15/20

DIMENSIONS ARE IN INCHES

INTERPRET GEOMETRIC TOLERANCING PER: ASME Y14.5-2009 | CHECKED | OST | 4/15/20

ENG APPR.

NONE FINISH | COMMENTS:

SCALE: 2:7 | WEIGHT:

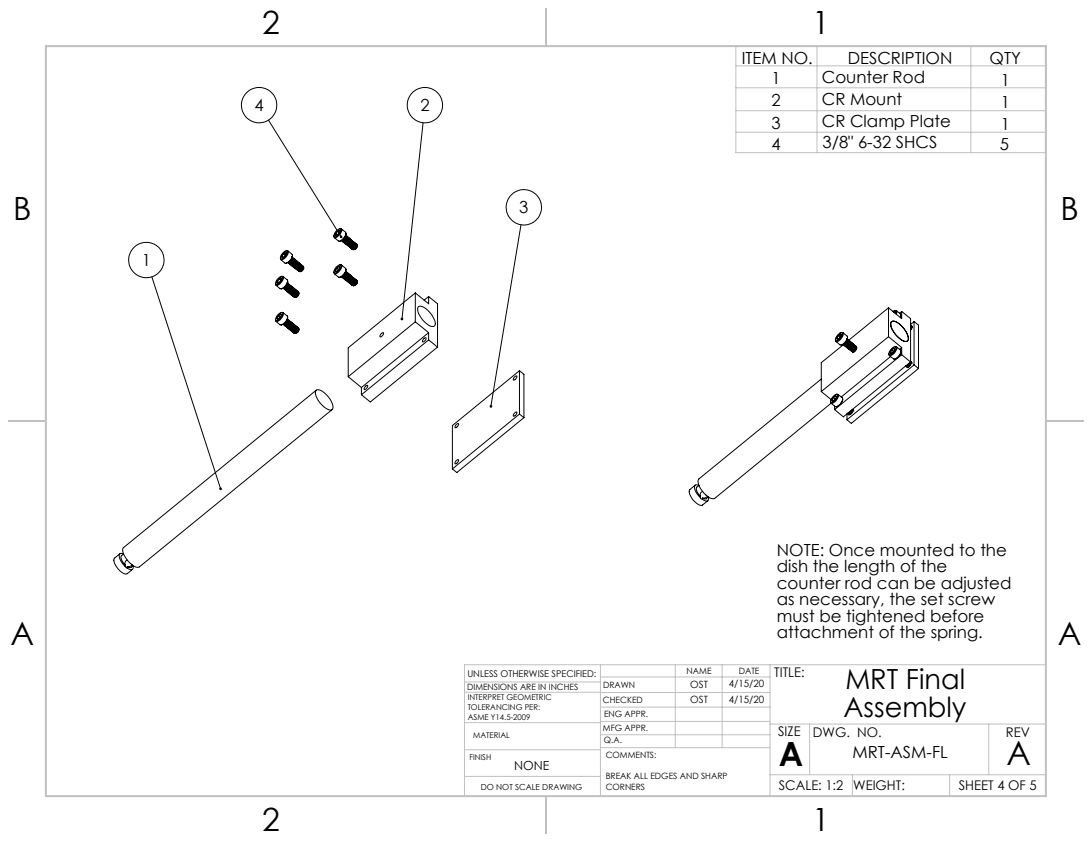
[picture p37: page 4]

1 | Counter Rod | 1
2 | CR Mount | 1
3 | CR Clamp Plate | 1
4 | 3/8" 6-32 SHCS | 5

NOTE: Once mounted to the
dish the length of the
counter rod can be adjusted
as necessary, the set screw
must be tightened before
attachment of the spring.

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

DRAWN | OST | 4/15/20

DIMENSIONS ARE IN INCHES

INTERPRET GEOMETRIC TOLERANCING PER: ASME Y14.5-2009 | CHECKED | OST | 4/15/20

ENG APPR.

NONE FINISH | COMMENTS:

SCALE: 1:2 | WEIGHT:

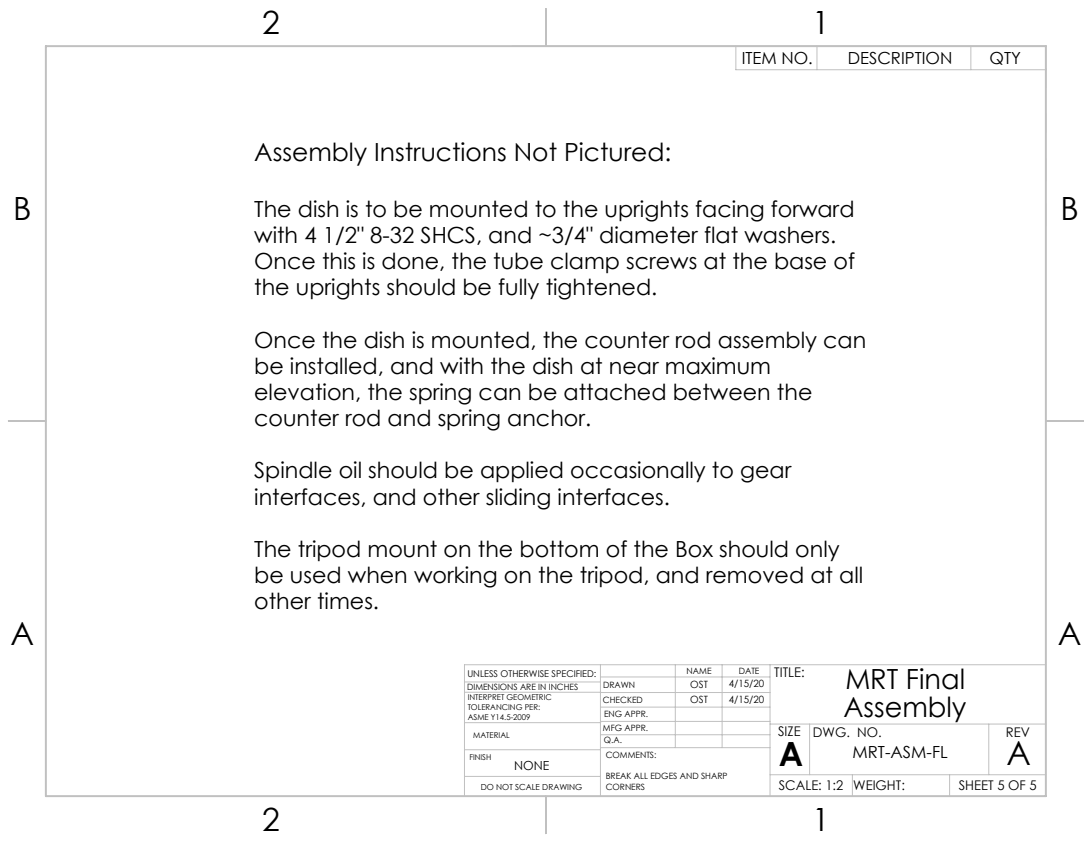
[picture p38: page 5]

Assembly Instructions Not Pictured:

The dish is to be mounted to the uprights facing forward
with 4 1/2" 8-32 SHCS, and ~3/4" diameter flat washers.
Once this is done, the tube clamp screws at the base of
the uprights should be fully tightened.
Once the dish is mounted, the counter rod assembly can
be installed, and with the dish at near maximum
elevation, the spring can be attached between the
counter rod and spring anchor.
Spindle oil should be applied occasionally to gear
interfaces, and other sliding interfaces.
The tripod mount on the bottom of the Box should only
be used when working on the tripod, and removed at all
other times.

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

DRAWN | OST | 4/15/20

DIMENSIONS ARE IN INCHES

INTERPRET GEOMETRIC TOLERANCING PER: ASME Y14.5-2009 | CHECKED | OST | 4/15/20

ENG APPR.

NONE FINISH | COMMENTS:

SCALE: 1:2 | WEIGHT:

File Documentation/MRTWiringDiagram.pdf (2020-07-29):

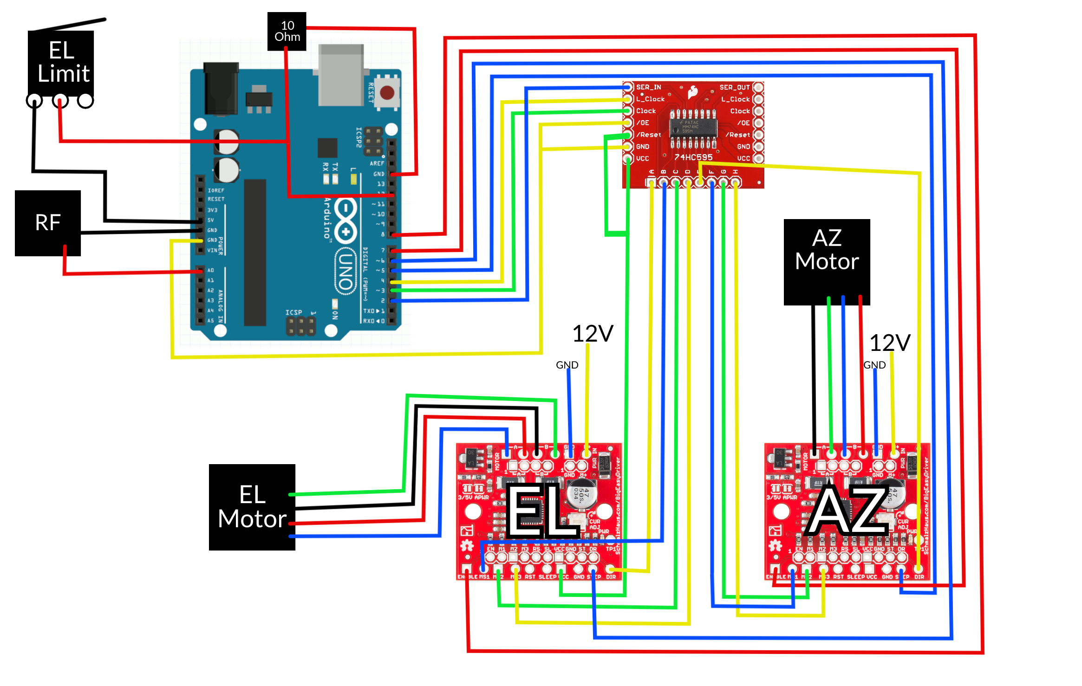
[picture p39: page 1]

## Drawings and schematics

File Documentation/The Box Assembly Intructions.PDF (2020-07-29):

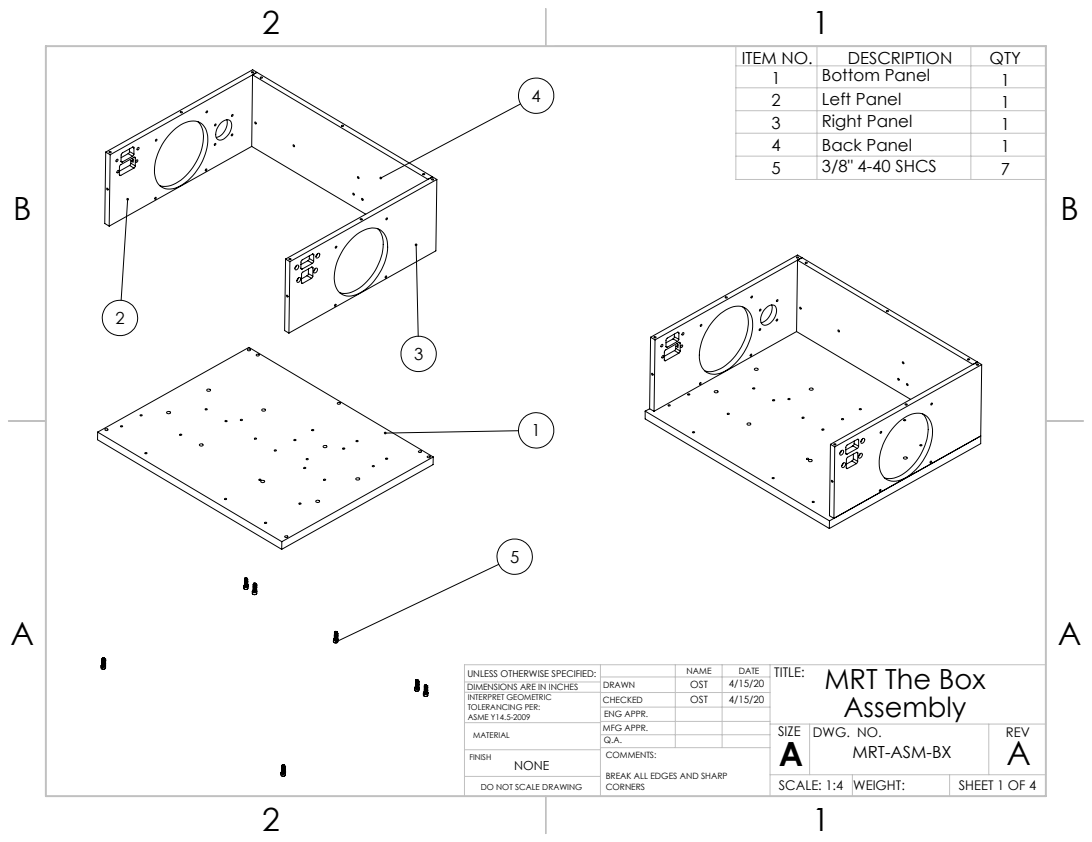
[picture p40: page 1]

ITEM NO. | DESCRIPTION | QTY
1 | Bottom Panel | 1
2 | Left Panel | 1
3 | Right Panel | 1
4 | Back Panel | 1
5 | 3/8" 4-40 SHCS | 7

UNLESS OTHERWISE SPECIFIED: | | NAME | DATE | MRT The Box TITLE: Assembly
MATERIAL | MFG APPR. | | | SIZE A | DWG. NO. MRT-ASM-BX | REV A

DRAWN | OST | 4/15/20

DIMENSIONS ARE IN INCHES

INTERPRET GEOMETRIC TOLERANCING PER: ASME Y14.5-2009 | CHECKED | OST | 4/15/20

ENG APPR.

NONE FINISH | COMMENTS: BREAK ALL EDGES AND SHARP CORNERS

DO NOT SCALE DRAWING | | SCALE: 1:4 | WEIGHT: | SHEET 1 OF 4

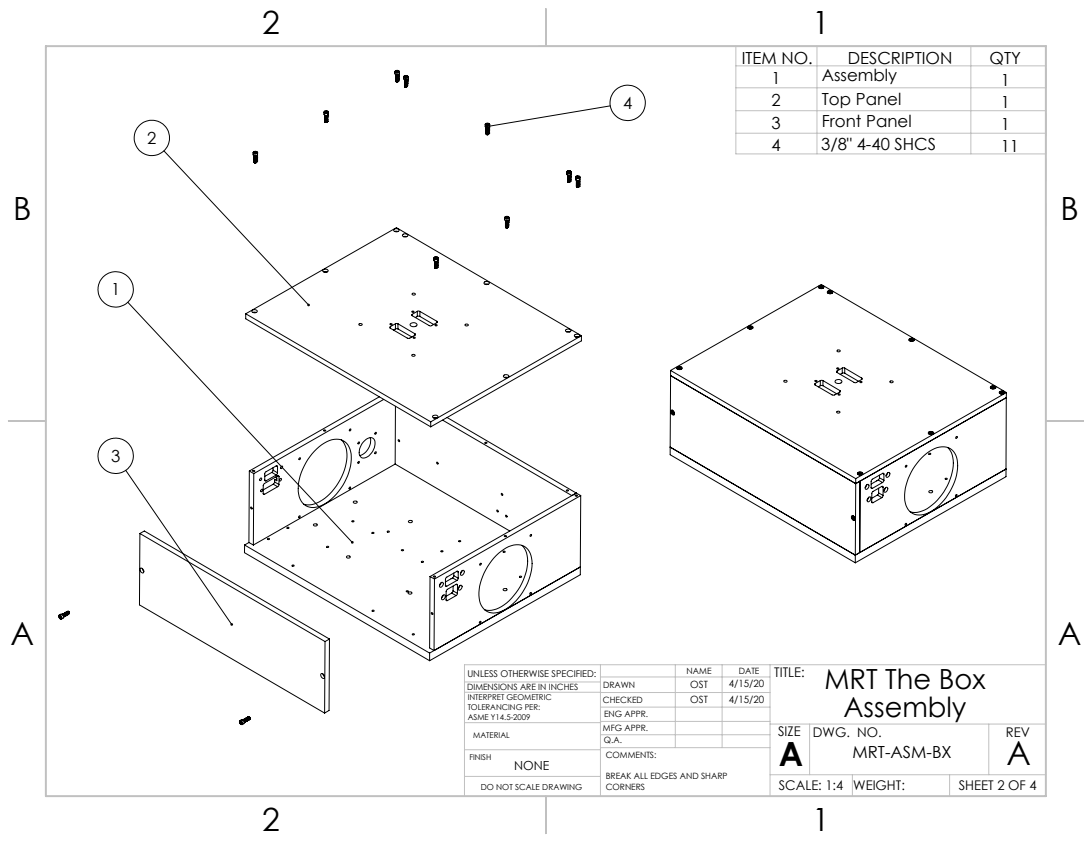
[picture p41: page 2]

1 | Assembly | 1
2 | Top Panel | 1
3 | Front Panel | 1
4 | 3/8" 4-40 SHCS | 11

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

DRAWN | OST | 4/15/20

DIMENSIONS ARE IN INCHES

INTERPRET GEOMETRIC TOLERANCING PER: ASME Y14.5-2009 | CHECKED | OST | 4/15/20

ENG APPR.

NONE FINISH | COMMENTS:

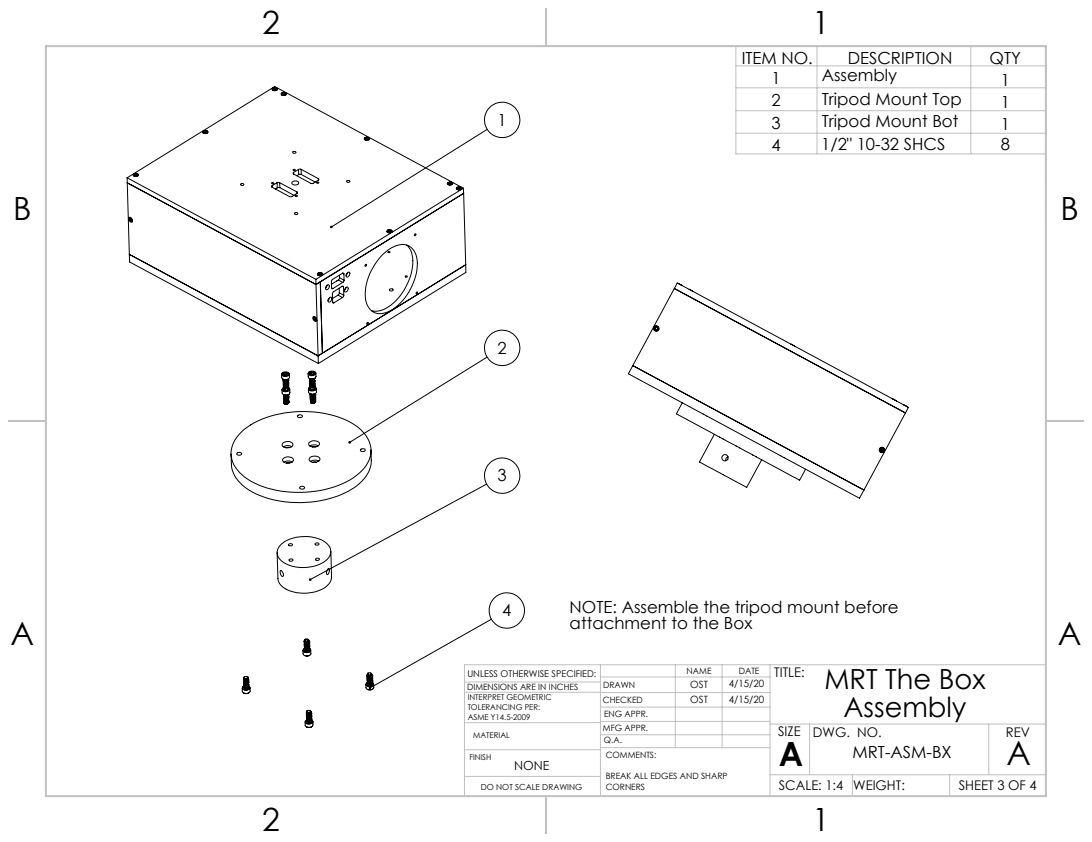
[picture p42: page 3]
NOTE: Assemble the tripod mount before

1 | Assembly | 1
2 | Tripod Mount Top | 1
3 | Tripod Mount Bot | 1
4 | 1/2" 10-32 SHCS | 8

attachment to the Box

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

DRAWN | OST | 4/15/20

DIMENSIONS ARE IN INCHES

INTERPRET GEOMETRIC TOLERANCING PER: ASME Y14.5-2009 | CHECKED | OST | 4/15/20

ENG APPR.

NONE FINISH | COMMENTS:

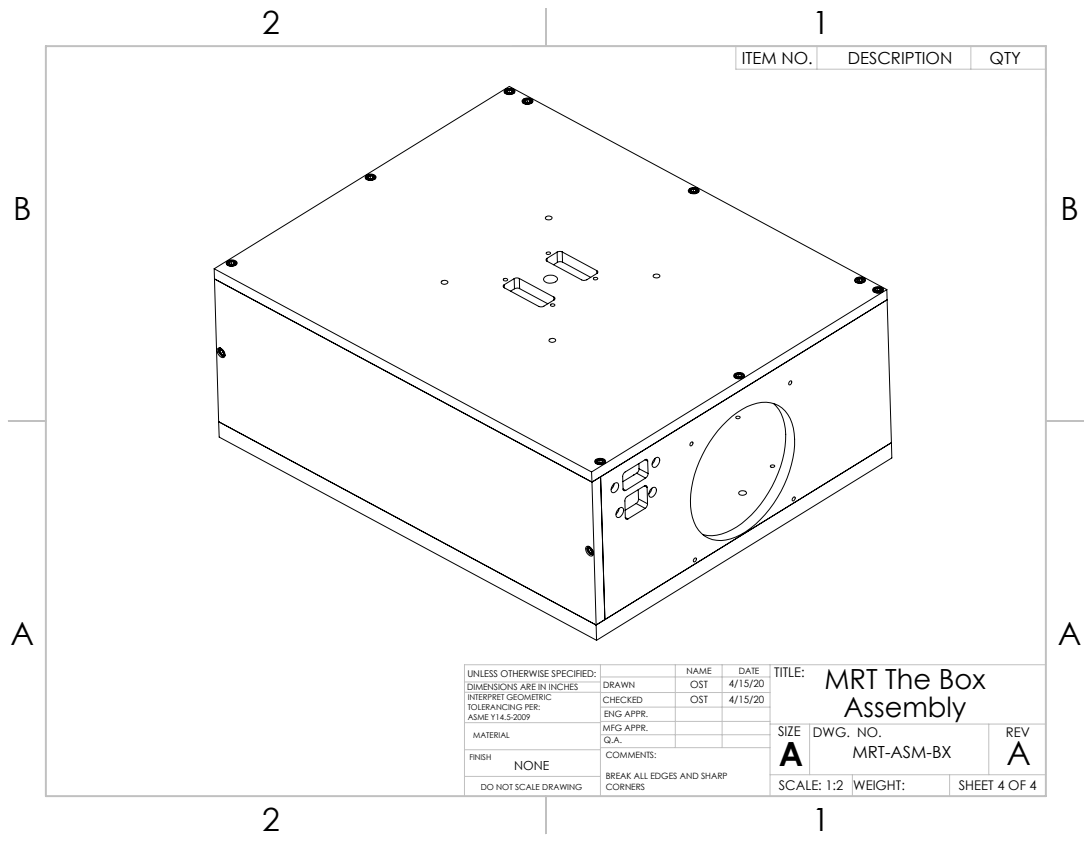
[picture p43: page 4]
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

DRAWN | OST | 4/15/20

DIMENSIONS ARE IN INCHES

INTERPRET GEOMETRIC TOLERANCING PER: ASME Y14.5-2009 | CHECKED | OST | 4/15/20

ENG APPR.

NONE FINISH | COMMENTS:

SCALE: 1:2 | WEIGHT:

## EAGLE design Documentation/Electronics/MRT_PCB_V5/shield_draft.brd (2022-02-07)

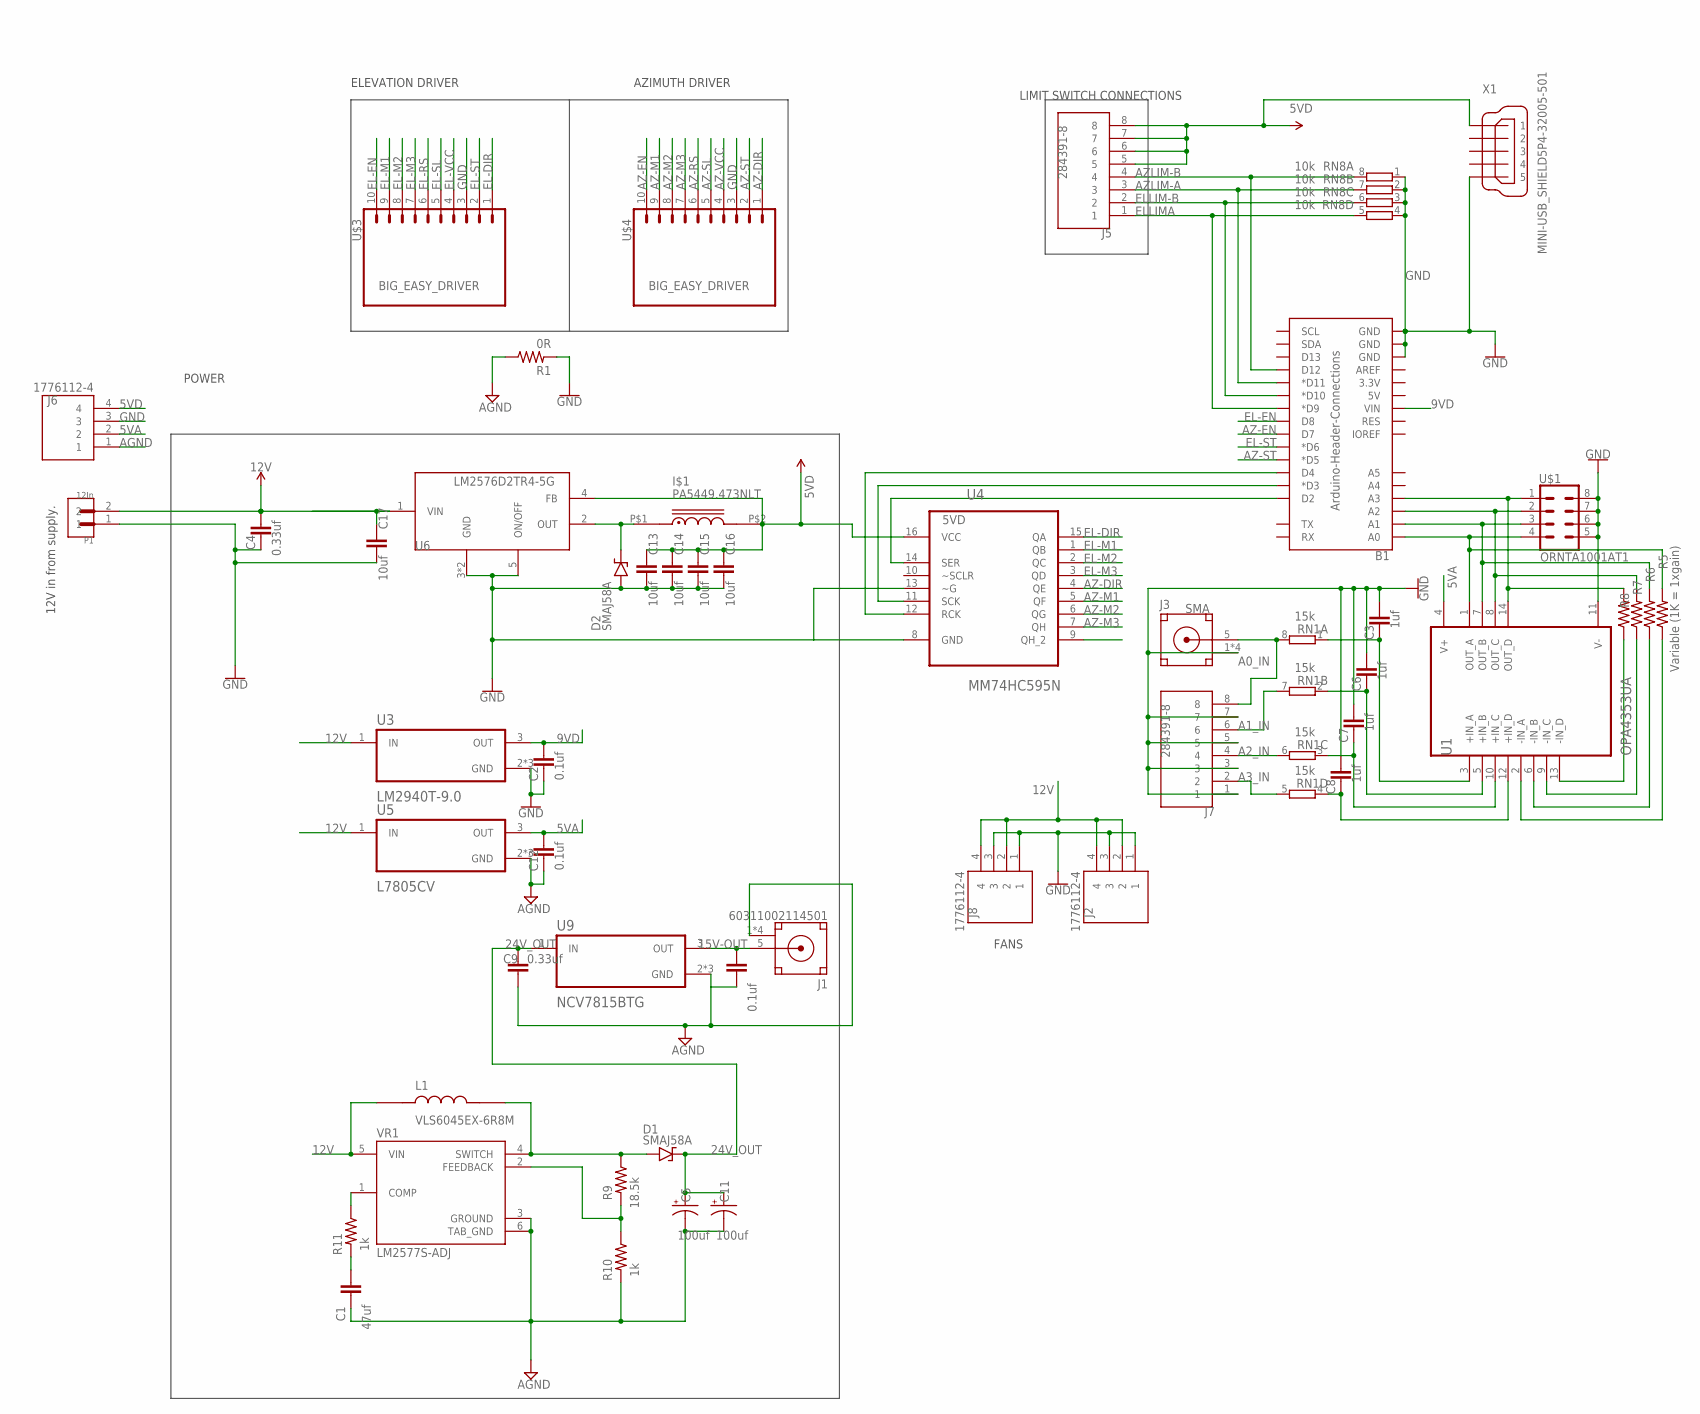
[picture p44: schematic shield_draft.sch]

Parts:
B1: Arduino-Header-Connections; UNO_R3_SHIELD
C1: 47uf; CAP_0805
C2, C10, C12: 0.1uf; CAP_0805
C3, C6, C7, C8: 1uf; CAP_0805
C4, C9: 0.33uf; CAP_0805
C5, C11: 100uf; E5-10,5
C13, C14, C15, C16, C17: 10uf; 0805
D1, D2: SMAJ58A; SMA
I$1: PA5449.473NLT; IND_TYS4020470M-10
J1: 60311002114501
J2, J6, J8: 1776112-4; TE_1776112-4
J3: SMA; 60311002114501
J5, J7: 284391-8; TE_284391-8
L1: VLS6045EX-6R8M; IND_VLS6045EX-6R8M
P1: 12In; OST_OSTTE020104
R1: 0R; 0603
R5: Variable (1K = 1xgain); RESAD1176W63L850D250B
R6, R7, R8: Var; RESAD1176W63L850D250B
R9: 18.5k; 0603
R10, R11: 1k; 0603
RN1: 15k; CAY16
RN8: 10k; CAY16
U1: OPA4353UA; SOIC127P600X175-14N
U3: LM2940T-9.0; TO254P1054X470X1955-3
U4: MM74HC595N; DIP254P762X533-16
U5: L7805CV; TO254P1054X470X1955-3
U6: LM2576D2TR4-5G; D2PAK-5
U9: NCV7815BTG; TO254P1054X470X1955-3
U$1: ORNTA1001AT1; SOIC127P600X175-8N
U$3, U$4: BIG_EASY_DRIVER; EASY_DRIVER_FTPRT
VR1: LM2577S-ADJ; TO170P1524X483-6N
X1: MINI-USB_SHIELD5P4-32005-501; 32005-501

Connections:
5VA: C12.2, J6.2, U1.4 (V+), U5.3 (OUT)
5VD: C13.1, C14.1, C15.1, C16.1, I$1.P$2 (2), J5.5, J5.6, J5.7, J5.8, J6.4, U4.16 (VCC), U6.4 (FB), X1.1
9VD: B1.VIN, C2.2, U3.3 (OUT)
12V: C4.2, C17.1, J2.2, J2.4, J8.2, J8.4, L1.1, P1.2, U3.1 (IN), U5.1 (IN), U6.1 (VIN), VR1.5 (VIN)
15V-OUT: C10.2, J1.5 (SIGNAL), U9.3 (OUT)
24V_OUT: C5.+, C9.2, C11.+, D1.C, U9.1 (IN)
24V_PRE: D1.A, L1.2, R9.1, VR1.4 (SWITCH)
A0_IN: J3.5 (SIGNAL), J7.8, RN1.8 (2)
A1_IN: J7.6, RN1.7 (2)
A2_IN: J7.4, RN1.6 (2)
A3_IN: J7.2, RN1.5 (2)
AGND: C1.1, C5.-, C9.1, C10.1, C11.-, C12.1, J1.1 (GND), J1.2 (GND), J1.3 (GND), J1.4 (GND), J6.1, R1.1, R10.2, U5.2 (GND), U5.P$1 (GND), U5.P$2 (GND), U9.2 (GND), U9.P$1 (GND), U9.P$2 (GND), VR1.3 (GROUND), VR1.6 (TAB_GND)
AIN+: C3.1, RN1.1, U1.3 (+IN_A)
AIN-: R5.1, U1.2 (-IN_A)
AZ-DIR: U4.4 (QE), U$4.1
AZ-EN: B1.D7, U$4.10
AZ-M1: U4.5 (QF), U$4.9
AZ-M2: U4.6 (QG), U$4.8
AZ-M3: U4.7 (QH), U$4.7
AZ-RS: U$4.6
AZ-SL: U$4.5
AZ-ST: B1.D5 (*D5), U$4.2
AZ-VCC: U$4.4
AZLIM-A: B1.D11 (*D11), J5.3, RN8.7 (2)
AZLIM-B: B1.D12, J5.4, RN8.8 (2)
A_OUT: B1.A0, R5.2, U1.1 (OUT_A), U$1.4 (R4A)
BIN+: C6.1, RN1.2 (1), U1.5 (+IN_B)
BIN-: R6.1, U1.6 (-IN_B)
B_OUT: B1.A1, R6.2, U1.7 (OUT_B), U$1.3 (R3A)
CIN+: C7.1, RN1.3 (1), U1.10 (+IN_C)
CIN-: R7.1, U1.9 (-IN_C)
C_OUT: B1.A2, R7.2, U1.8 (OUT_C), U$1.2 (R2A)
DIN+: C8.1, RN1.4 (1), U1.12 (+IN_D)
DIN-: R8.1, U1.13 (-IN_D)
D_OUT: B1.A3, R8.2, U1.14 (OUT_D), U$1.1 (R1A)
EL-DIR: U4.15 (QA), U$3.1
EL-EN: B1.D8, U$3.10
EL-M1: U4.1 (QB), U$3.9
EL-M2: U4.2 (QC), U$3.8
EL-M3: U4.3 (QD), U$3.7
EL-RS: U$3.6
EL-SL: U$3.5
EL-ST: B1.D6 (*D6), U$3.2
EL-VCC: U$3.4
ELLIM-B: B1.D10 (*D10), J5.2, RN8.6 (2)
ELLIMA: B1.D9 (*D9), J5.1, RN8.5 (2)
GND: B1.GND@0 (GND), B1.GND@1 (GND), B1.GND@2 (GND), C2.1, C3.2, C4.1, C6.2, C7.2, C8.2, C13.2, C14.2, C15.2, C16.2, C17.2, D2.A, J2.1, J2.3, J3.1 (GND), J3.2 (GND), J3.3 (GND), J3.4 (GND), J6.3, J7.1, J7.3, J7.5, J7.7, J8.1, J8.3, P1.1, R1.2, RN8.1, RN8.2 (1), RN8.3 (1), RN8.4 (1), U1.11 (V-), U3.2 (GND), U3.P$1 (GND), U3.P$2 (GND), U4.8 (GND), U4.13 (~G), U6.3 (GND), U6.5 (ON/OFF), U6.6 (GND), U$1.5 (R4B), U$1.6 (R3B), U$1.7 (R2B), U$1.8 (R1B), U$3.3, U$4.3, X1.5
unnamed: B1.D2, U4.14 (SER)
unnamed: R9.2, R10.1, VR1.2 (FEEDBACK)
unnamed: D2.C, I$1.P$1 (1), U6.2 (OUT)
unnamed: R11.1, VR1.1 (COMP)
unnamed: C1.2, R11.2
unnamed: B1.D3 (*D3), U4.11 (SCK)
unnamed: B1.D4, U4.12 (RCK)

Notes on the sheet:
POWER
ELEVATION DRIVER
AZIMUTH DRIVER
LIMIT SWITCH CONNECTIONS
12V in from supply.
FANS

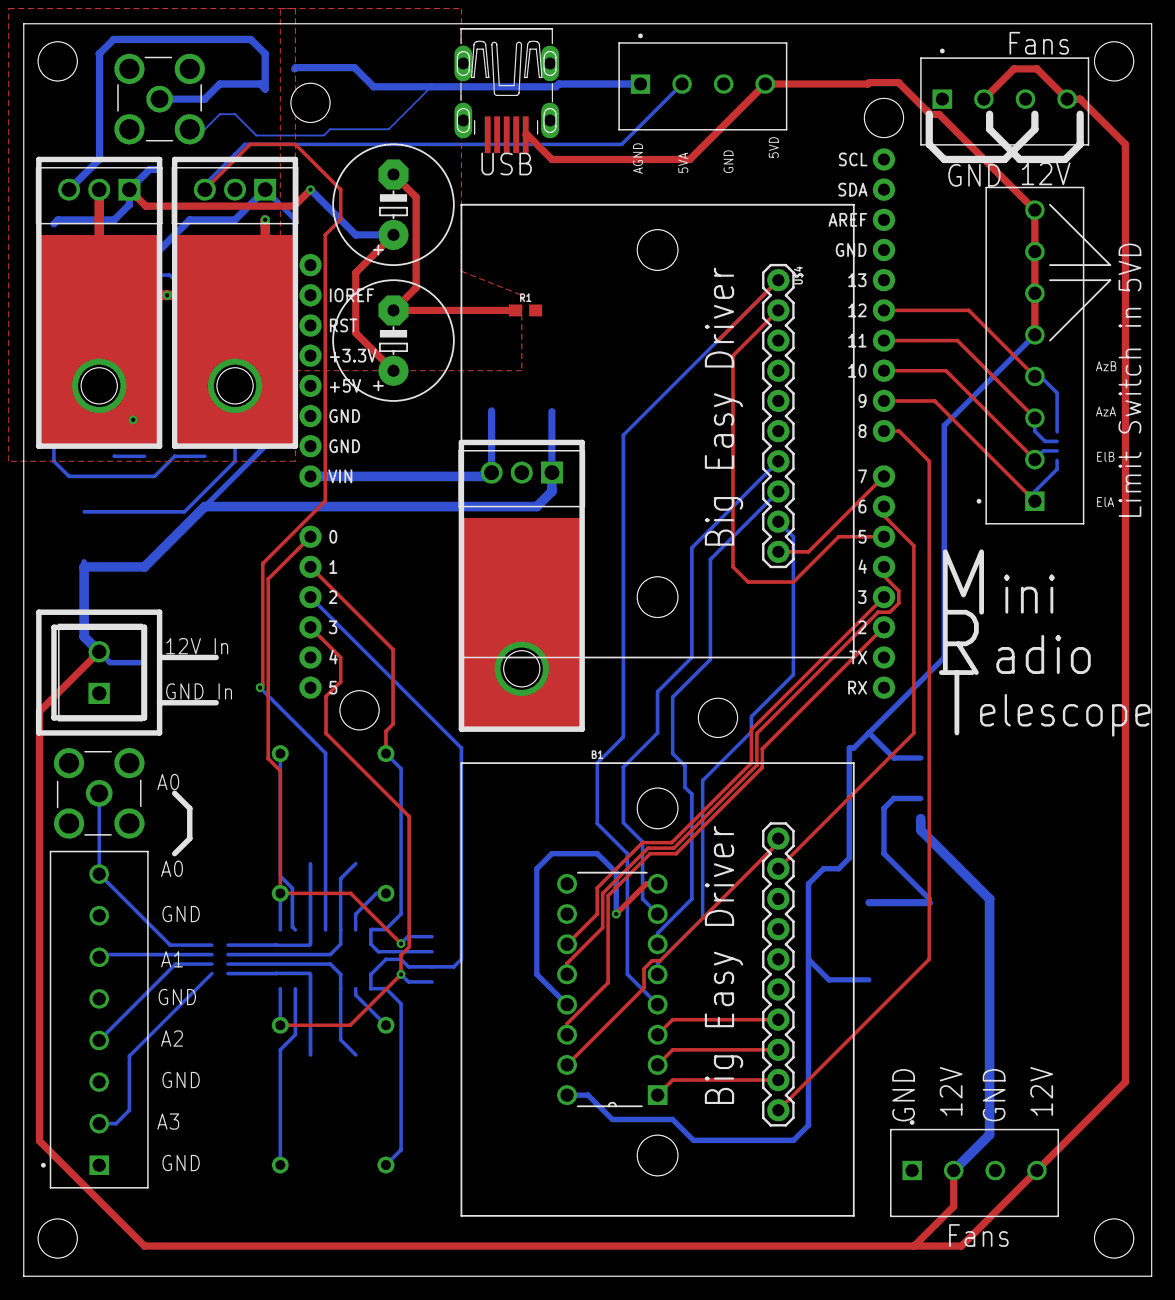
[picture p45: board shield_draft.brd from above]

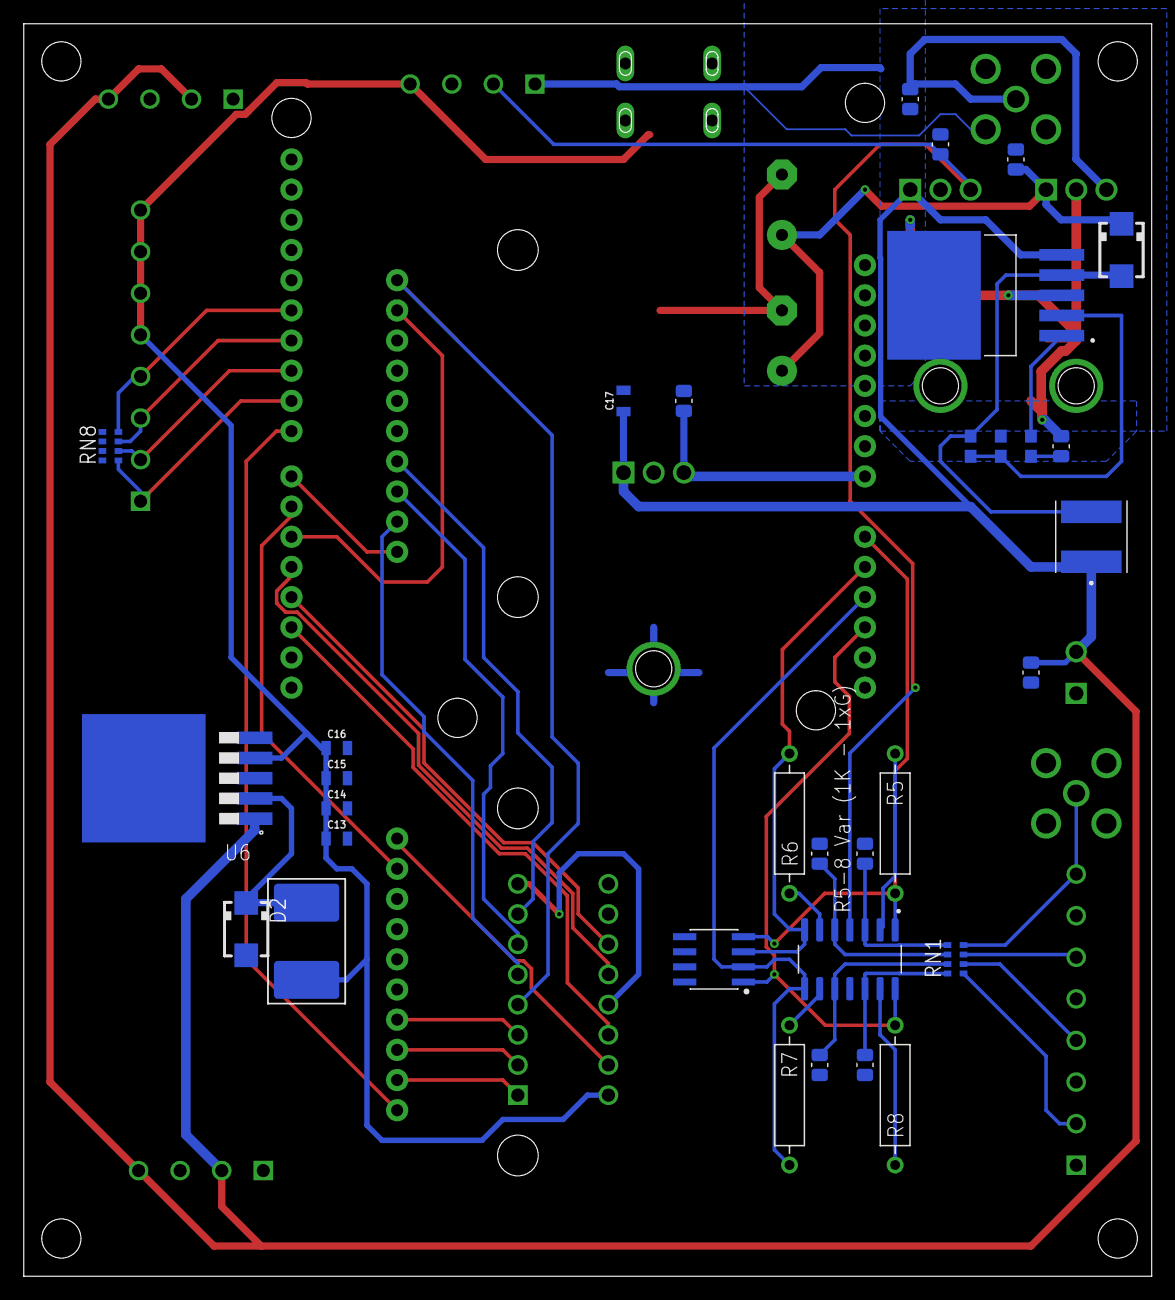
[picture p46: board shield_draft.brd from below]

Board: 2 copper layers, 94.9 x 105.4 mm, 59 parts (32 on the bottom side), 48 nets.

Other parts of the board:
JP1, JP2, JP3, JP4, JP5, JP6, JP7, JP10: STAND-OFF

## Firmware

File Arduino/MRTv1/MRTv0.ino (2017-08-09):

// Updated and tested with Arduino not connected to telescope 27 March 2017

/****************************************************************************** 
SparkFun Big Easy Driver Basic Demo
Toni Klopfenstein @ SparkFun Electronics
February 2015
https://github.com/sparkfun/Big_Easy_Driver

Simple demo sketch to demonstrate how 5 digital pins can drive a bipolar stepper motor,
using the Big Easy Driver (https://www.sparkfun.com/products/12859). Also shows the ability to change
microstep size, and direction of motor movement.

Development environment specifics:
Written in Arduino 1.6.0

This code is beerware; if you see me (or any other SparkFun employee) at the local, and you've found our code helpful, please buy us a round!
Distributed as-is; no warranty is given.

Example based off of demos by Brian Schmalz (designer of the Big Easy Driver).
http://www.schmalzhaus.com/EasyDriver/Examples/EasyDriverExamples.html
******************************************************************************/
//Declare pin functions on Arduino

#define ELSTP 2  // 2  ST
#define ELDIR 3  // 3  DR
#define ELMS1 4  // 4  M1
#define ELMS2 5  // 5  M2
#define ELMS3 6  // 6  M3
#define ELEN  7  // 7  EN

#define AZSTP 9  // 2   ST
#define AZDIR 8  // 3   DR
#define AZMS1 11 // 4  M1
#define AZMS2 12 // 5  M2
#define AZMS3 13 // 6  M3
#define AZEN  10 // 7  EN

#define GEAR_RATIO 8
#define DEGREES_PER_STEP 1.8
#define MICRO_STEPS 16

#define BTX "AAA"
#define EOT "ZZZ"
#define BDTX "BDTX"
#define EDTX "EDTX"

#define BLCKAVG 16

int STP; 
int DIR; 
int MS1; 
int MS2; 
int MS3; 
int EN;  

//Declare variables for functions
char user_input;
//int x;
//int y;
// int state;

// Ugh.  Don't actually HAVE the current state of either axis

// Current position of elevation axis
float elCurrDeg;
int elCurrSteps;
int elCurrMicroSteps;
// Current position of azimuth axis
float azCurrDeg;
int azCurrSteps;
int azCurrMicroSteps;

char stepping_mode; 
float degrees_to_turn; 
int rot_sense;
char current_axis;
//char rot_dir // How does one get a string variable?

int analogPin = 0;
int val;
float voltage;

float NormAdd, MicroAdd;

void setup(){
  
  pinMode(AZSTP, OUTPUT);
  pinMode(AZDIR, OUTPUT);
  pinMode(AZMS1, OUTPUT);
  pinMode(AZMS2, OUTPUT);
  pinMode(AZMS3, OUTPUT);
  pinMode(AZEN, OUTPUT);
  pinMode(ELSTP, OUTPUT);
  pinMode(ELDIR, OUTPUT);
  pinMode(ELMS1, OUTPUT);
  pinMode(ELMS2, OUTPUT);
  pinMode(ELMS3, OUTPUT);
  pinMode(ELEN, OUTPUT);
  SetAxis('A');
  resetBEDPins(); //Set step, direction, microstep and enable pins to default states
  elCurrSteps = 0;
  elCurrDeg = 0;
  elCurrMicroSteps = 0;
  azCurrSteps = 0;
  azCurrDeg = 0;
  azCurrMicroSteps = 0;
  stepping_mode = 'N';
  rot_sense = 1;
  
  // Finally, open serial connection
  Serial.begin(115200); //Open Serial connection for debugging
  Serial.println("ARDUINO MRT");
  //Serial.println(EOT);
  PrintMenu();
 
}

//Main loop
void loop() {
  while(Serial.available()){
      user_input = Serial.read(); //Read user input and trigger appropriate function
      if((user_input == 'E') || (user_input == 'D'))
      {
        SetEnable(user_input);
      } else if ((user_input == 'F') || (user_input == 'R'))
      {
        SetDirection(user_input);
      }
      else if ((user_input == 'A') || (user_input == 'L'))
      {
        SetAxis(user_input);
      }
      else if((user_input == 'N') || (user_input == 'M'))
      {
        SetStepMode(user_input);
      }
      else if(user_input == 'S')
      {
        while (Serial.available()==0){ }
        degrees_to_turn = Serial.parseFloat();
        RotateDegrees(degrees_to_turn);
      }
      else if(user_input == 'Z'){
        Serial.println("Zeroing position.");
        elCurrSteps = 0;
        elCurrDeg = 0;
        elCurrMicroSteps = 0;
        azCurrSteps = 0;
        azCurrDeg = 0;
        azCurrMicroSteps = 0;       
      }
      else
      {
        Serial.println("Invalid option entered.");
        Serial.println(EOT);
      }
      //resetBEDPins();
      PrintState();
      PrintMenu();
  }
}

void PrintMenu()
{
  //Print function list for user selection
  Serial.println("Enter motor control option:");
  Serial.println("E for Enable; D for Disable");
  Serial.println("F for Forward; R for Reverse");
  Serial.println("A for azimuth; L for elevation");
  Serial.println("N for normal steps; M for microsteps");
  Serial.println("S turn a number of decimal degrees");
  Serial.println("Z to zero the angle counter");
  Serial.println();
  Serial.println(EOT);
}

void PrintState()
{
  Serial.println();
  Serial.print("Active axis: ");
  if (current_axis=='A'){
    Serial.println("AZ");
  } else{
    Serial.println("EL");
  }
  Serial.print("Rotation sense: ");
  // Ugly.  Gotta have a better way of knowing the internal state
  if (current_axis=='A'){
    if (rot_sense==1){
      Serial.println("CCW");
    } else {
      Serial.println("CW");
    }
  } else{
    if (rot_sense ==1){
      Serial.println("Inc");
    } else {
      Serial.println("Dec");
    }
  }
  Serial.println("Current position");
  Serial.print("AZ: ");
  Serial.print(azCurrDeg);
  Serial.print("  EL: ");
  Serial.println(elCurrDeg);
  Serial.println();
}

//Reset Big Easy Driver pins to default states
void resetBEDPins()
{
  digitalWrite(STP, LOW);
  digitalWrite(DIR, LOW);
  digitalWrite(MS1, LOW);
  digitalWrite(MS2, LOW);
  digitalWrite(MS3, LOW);
  digitalWrite(EN, HIGH); // Motor is off at power-on
}

void SetEnable(char enable)
{
  if (enable == 'E')
  {
    digitalWrite(EN, LOW); 
    Serial.println("Motor enabled.");
  }
  else if (enable == 'D')
  {
    digitalWrite(EN, HIGH); 
    Serial.println("Motor disabled.");
  }
}

void SetDirection(char direction)
{
  if (direction == 'F')
  {
    digitalWrite(DIR, LOW); //Pull direction pin low to move "forward"
    rot_sense = 1;
    
    Serial.println("Direction set to forward.");
  }
  else if (direction == 'R')
  {
    digitalWrite(DIR, HIGH); //Pull direction pin low to move "backward"
    rot_sense = -1;
    Serial.println("Direction set to backward."); 
  }
}

void SetAxis(char axis)
{
  if (axis == 'A'){
    STP = AZSTP;
    DIR = AZDIR;
    MS1 = AZMS1;
    MS2 = AZMS2;
    MS3 = AZMS3;
    EN = AZEN;
    current_axis = 'A';
  } else if (axis == 'L'){
    STP = ELSTP;
    DIR = ELDIR;
    MS1 = ELMS1;
    MS2 = ELMS2;
    MS3 = ELMS3;
    EN = ELEN;
    current_axis = 'L';
  }
  Serial.print("Set axis to ");
  if (current_axis=='A'){
    Serial.println("AZ");
  } else{
    Serial.println("EL");
  }
  
}

void SetStepMode(char mode)
{
  if (mode == 'N') // Default
  {
    digitalWrite(MS1, LOW);
    digitalWrite(MS2, LOW); 
    digitalWrite(MS3, LOW);
    Serial.println("Default step set.");
  } else if (mode == 'M')
  {
    digitalWrite(MS1, HIGH); //Pull MS1,MS2, and MS3 high to set logic to 1/16th microstep resolution
    digitalWrite(MS2, HIGH);
    digitalWrite(MS3, HIGH); 
    Serial.println("Micro (1/16) step set.");   
  }
  stepping_mode = mode;
}

float ReadRadioADC(int ndata)
{
  int cnt;
  voltage = 0.;
  //Serial.println(BDTX);
  for(cnt= 1; cnt<ndata; cnt++)  
  {
    // Read the ADC for the radiometer
    val = analogRead(analogPin);
    voltage += 5.0*val/1024.;
    //Serial.println(voltage,5);
  }
  //Serial.println(EDTX);
  voltage /= ndata;
  return voltage;
}

void TakeSteps(int steps)
{
  long x;
  float voltaccum[BLCKAVG];
  int avg, cnt = 0;
  
  //Serial.println(STP);
  for(x= 1; x<steps; x++)  
  {
    digitalWrite(STP,HIGH); //Trigger one step forward
    delay(1);
    digitalWrite(STP,LOW); //Pull step pin low so it can be triggered again
    delay(1);

    if (stepping_mode == 'M'){
      NormAdd = 1./16.;
      MicroAdd = 1;
    } 
    else {
      NormAdd = 1;
      MicroAdd = 16; 
    }
    if (current_axis == 'L'){
      elCurrSteps += rot_sense * NormAdd;
      elCurrMicroSteps += rot_sense * MicroAdd;
      elCurrDeg += rot_sense * Steps2Degrees(1,stepping_mode);
    } else{
      azCurrSteps += rot_sense * NormAdd;
      azCurrMicroSteps += rot_sense * MicroAdd;
      azCurrDeg += rot_sense * Steps2Degrees(1,stepping_mode);
    }

    // Read the ADC for the radiometer
    //val = analogRead(analogPin);
    //voltage = 5.0*val/1024.;
    
    voltage = ReadRadioADC(10);
    voltaccum[cnt] = voltage;
    cnt++;
    if (x%BLCKAVG == 0){
      voltage = 0.;
      cnt = 0;
      for(avg=1; avg<BLCKAVG; avg++){
        voltage += voltaccum[avg];
      }
      voltage /= float(BLCKAVG);
      Serial.print(azCurrDeg,5);
      Serial.print("  ");
      Serial.print(elCurrDeg,5);
      Serial.print("  ");
      Serial.println(voltage,5);
    }
  }
}

int Degrees2Steps(float deg, char mode){
  int nSteps;
  nSteps = int(deg / DEGREES_PER_STEP * GEAR_RATIO);
  if (mode == 'M'){
    nSteps *= MICRO_STEPS;
  }
  return nSteps;
}

float Steps2Degrees(int steps, char mode){
  float deg;
  deg = float(steps)*DEGREES_PER_STEP/float(GEAR_RATIO);
  if (mode == 'M'){
    deg /= float(MICRO_STEPS);
  }
  return deg;
}

void RotateDegrees(float deg)
{
  int nSteps, nMicroSteps;
  //float actual_degrees;
  
  //Serial.print("Turning ");
  //Serial.print(deg);
  //Serial.println(" degrees.");
  
  // Calculate both steps and microsteps
  nSteps = Degrees2Steps(deg, 'N');
  nMicroSteps = Degrees2Steps(deg, 'M');

  //Serial.println(BTX);
  /* Which thing is commanded and how actual degrees are calculated depends on 
  the mode */
  if (stepping_mode == 'N')
  {
    Serial.println(BDTX);
    TakeSteps(nSteps);
    Serial.println(EDTX);
    //actual_degrees = Steps2Degrees(nSteps,'N');
  } else
  {
    Serial.println(BDTX);
    TakeSteps(nMicroSteps);
    Serial.println(EDTX);
    //actual_degrees = Steps2Degrees(nMicroSteps,'M');
  }
}

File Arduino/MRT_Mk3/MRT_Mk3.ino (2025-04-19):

/*

Most recent update 18 April 2025.

 If the full command is not read in one dt_loop length time, I think the command just fails
 This does not seem to happen a lot in practice
 Ill-formed commands are simply ignored 
 
 The data reporting rate and the maximum rate at which the motor steps can be changed are the same.  
 Slower steps are possible with the "clock cycles per step" part of the command
 */

 // ADC operation
 int analogPin = 0;
 float voltage;

//Declare pin functions on Arduino DIO
#define datapin 2
#define clockpin 3
#define latchpin 4
#define ELSTP 6  // 5  ST
#define AZSTP 5  // 6  ST
#define ELEN 8 // 7 EN
#define AZEN 7 // 8 EN
#define ELIMIT 12 // lower limit switch

// Pins on the shift register
#define ELDIR 0  // 0 index of shift register
#define ELMS1 1  // 1 index of shift register
#define ELMS2 2  // 2 index of shift register
#define ELMS3 3  // 3 index of shift register
#define AZDIR 4  // 4 index of shift register
#define AZMS1 5  // 5 index of shift register
#define AZMS2 6  // 6 index of shift register
#define AZMS3 7  // 7 index of shift register
//need this one for shift register
byte data = 0;

#define BAUD_RATE 115200

//Variables that change which pin they they refer to depending on which axis is selected
int STP;
int DIR;
int MS1;
int MS2;
int MS3;
int EN;

/*
 Commands will have the form:

  Axis / Sense / Microstep / Clock cycles per step / Number of steps

  Axis: "a" for azimuth or "e" for elevation

  Sense: "+" or "-" defined as 
    elevation: + = increasing elevation
    azimtuth: + = CCW?

  Microstep: "m", e, q, h, f: whether the motor controller microsteps or full steps (with gradations between)
    Generally "m" is the right call for smooth operation.

  Clock cycles per step: up to 4 chars, specifying an interger.  How many clock cycles (dt_loop) per motor step as set above.  0001 has the steps occurring as fast as
    the loop executes; larger numbers will slow down the rate at which the steps are sent

  Number of steps: up to 5 chars
 
 */

#define CMDLENGTH 12;
 
char axis = 'x', sense='x', step_mode='x';
const byte Ncps_char = 5;
const byte Nstep_char = 6;
char N_cch_char[Ncps_char] = "xxxx"; 
char number_of_steps_char[Nstep_char] = "xxxxx";
int N_cch; // Number of clock cycles (loops) per half of a step
int number_of_steps;
int i;
int NreceivedChars = 0;


const byte numChars = 32;
char receivedChars[numChars] = "xxxxxxxxxxxx";
char last_command[numChars];

boolean newData = false;

unsigned long t1, t2, dt;
unsigned long dt_loop = 4000; // microseconds; this should be fast
unsigned long counter = 0;

signed long az_steps = 0;
signed long el_steps = 0;
signed long steps[2] = {0,0};

/* 
need to have a protocol for what to do if we receive a new command while executing an existing one.
for now, let's have it be blocking ... tested that this does work.  Commands sent while others are executing are ignored.
This means only one axis can move at a time, AND the overall control program needs to check if the command has completed.
*/
boolean executingCmd = false; 

boolean first_half = true, transition = true;
int n_steps_remaining = 0;
int n_half = 0; 
char stepstate = 'n';
int sign = 0;
int axindx = 0;
int step_size = 0;

void setup() {
  // put your setup code here, to run once:

  // Setup of DIO pins
  pinMode(AZEN, OUTPUT);
  pinMode(ELEN, OUTPUT);
  pinMode(AZSTP, OUTPUT);
  pinMode(ELSTP, OUTPUT);
  pinMode(datapin, OUTPUT);
  pinMode(clockpin, OUTPUT);
  pinMode(latchpin, OUTPUT);
  pinMode(ELIMIT, INPUT);

  // Disable the motors by default
  digitalWrite(AZEN, HIGH);
  digitalWrite(ELEN, HIGH);

  // Finally, open serial connection
  Serial.begin(115200); //Open Serial connection for debugging
  //Serial.println("ARDUINO MRT Mk3");

}
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

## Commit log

2016-07-15 Arduino code for the LMS9DS1 sensor and separately for motor control
2016-07-18 Trying to make a python version of the Arduino serial monitor
2016-07-20 pyArduinoSerialTerminal.py basically reproduces the Arduino Serial Monitor functionality now, though there is a bit of an offset between when the Arduino sends something to the buffer and this progra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
2016-07-29 A serial communication tester for Arduino
2016-07-29 Working simple serial communication with Arduino
2016-08-10 Making the Arduino stuff more organized
2016-08-10 One more Arduino ino
2016-08-10 Pseudo-working Arduino and Python serial
2016-12-14 Current working version
2018-04-12 Thu Apr 12 12:15:35 EDT 2018
    [CommissioningData04112018.xlsx]
2018-07-12 Fully functional with some new modifications, including variable dimensions in mapping and a print menu function.
2019-07-18 Wed Jul 17 21:02:56 EDT 2019
    [CommissioningData04112018.xlsx]
2019-11-13 Added Sample Scan and Map Plots
2020-03-31 Created new Arduino code based on CNC G-Code. To be used for code development without telescope hardware.
2020-07-06 Small bug fixes, refresh button for current readings, started working on connecting the Arduino
2020-07-11 Auto find of Arduino port and connection.
2020-08-06 Matched mrtstate with Arduino code. Moved serial to main program and changed FUNC to match.
2021-02-16 Making directory name conform to Arduino convention
2022-02-07 adding the PCB schematics
    [copper_bottom.gbr, copper_top.gbr, drill_1_16.xln, gerber_job.gbrjob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]

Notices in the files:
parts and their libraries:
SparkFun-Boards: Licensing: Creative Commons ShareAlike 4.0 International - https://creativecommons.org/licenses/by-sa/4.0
